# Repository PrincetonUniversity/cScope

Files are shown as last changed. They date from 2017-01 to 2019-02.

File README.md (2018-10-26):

# cScope 
A Head Mounted Widefield Macroscope 

This Github repository is meant to distribute the files accompanying the manuscript "Imaging cortical dynamics in GCaMP transgenic rats with a head-mounted widefield macroscope" by Benjamin Scott, Stephan Thiberge, Caiying Guo, Dougal Tervo, Carlos Brody, Alla Karpova, David Tank to appear in Neuron Journal (https://doi.org/10.1016/j.neuron.2018.09.050).

The repository contains the hardware information needed to build the cScope macroscopes, and the software needed to run experiments and post-process the data.

Use the "Clone or Download" button on this page, and choose "Download .Zip" to download all the files contained in this repository. Alternatively, you can download individual files by navigating through the repository folders.

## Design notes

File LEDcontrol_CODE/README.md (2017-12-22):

# LEDs control

The Arduino folder contains the two arduino codes, DELAY and GATE, loaded respectively on Arduino 1 and Arduino 2 (see manuscript supplemental figure). 
For each arduino, two versions of the code are written for different camera speeds (frame rate of 30Hz and 60Hz).

The Matlab folder contains the code run on the "LED control" computer.

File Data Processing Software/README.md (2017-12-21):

# Data Processing Software

Included in this directory are MATLAB scripts for processing the data files generated by cScope.  In order to run these scripts you will need to have a folder containing the .avi files and a timestamp.dat file that are produced by the miniscope camera acquisition system.  We assume that you will also have a data file produced by the Bcontrol software available here: http://brodywiki.princeton.edu/bcontrol/index.php/Main_Page

In order to run the motion correction stage in the preprocessing pipeline you will also need to download NoRMCorre:
https://github.com/simonsfoundation/NoRMCorre

Proceed in the following order:
1) cScope_preprocessing (~ 1 hour)
2) Hemodynamic_correction or Hemodynamic_correction_version2 (~ 12 hours)
3) Widefield_analysis (< 1 hour)

Included in parentheses are the approximate runtimes for processing a ~150,000 frame movie on a MacBookPro with a 3.1 GHz Intel Core i7 processor and 16 GB 1867 MHz DDR3 memory.

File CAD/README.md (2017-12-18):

# CAD files

The DWFX file is best viewed with the online viewer from Autodesk (viewer.autodesk.com). It allows the whole cScope assembly to be visualized in 3D and facilitates its construction.

The "3D printed parts" folder contains the .STL files for all printed parts used in cScope. These files can be uplaoded and used directly for 3d printing. We have used the company 3dsystems.com and the following process, materials and finish: Process: Stereolithography (SLA), Material: High-Res ABS-Like Black (either Accura SL 7820, or Renshape 7820 / VisiJet SL Black), Standard Finish. When asked for units during order process, enter "mm". 

The "machineshop" folder contains the drawings for the few parts that require machining.

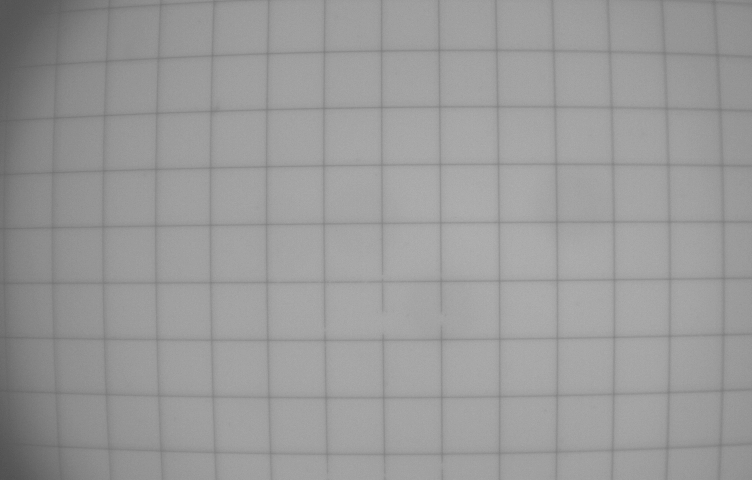
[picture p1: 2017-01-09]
DeformationCorrection/500umGrid.png

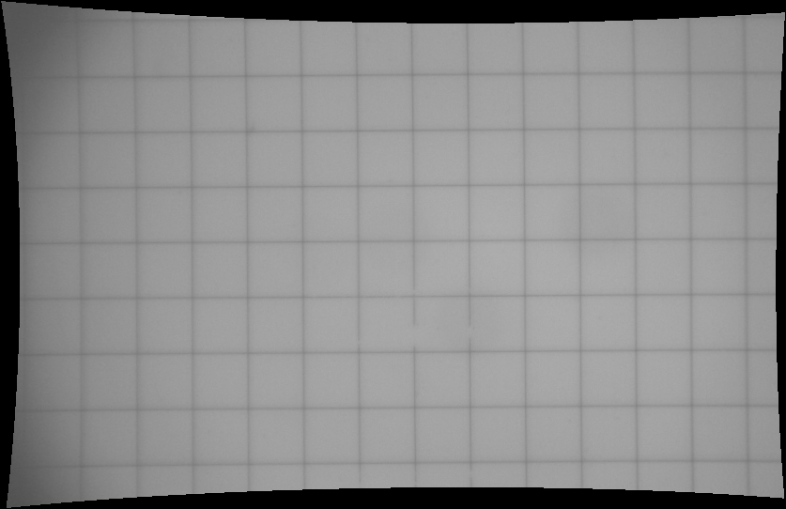
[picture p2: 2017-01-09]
DeformationCorrection/500umGrid_Unwarped.png

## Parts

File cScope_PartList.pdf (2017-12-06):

List of components for cScope. "Imaging cortical dynamics in GCaMP transgenic rats with a head mounted widefield macroscope” by Scott et al.

Label | Quantity | Unit | Part Number | Suggested Vendor | Description | Link | Approxi. Cost | Notes
| Lenses
CrW | 1 Ea | Custom part | TowerOptical
| | | | | N-BK7 Glass, 8mm*8mm, 3mm thick, flatness lambda/4 @ 633 nm, Surf
80/50 Scratch- Dig | http://www.toweroptical.com/ $13 Custom window, price/unit is for 25 units order
CrW | 1 Ea | Custom part | TowerOptical
| | | | | N-BK7 Glass, 8mm*4mm, 3mm thick, flatness lambda/4 @ 633 nm, Surf
80/50 Scratch- Dig | http://www.toweroptical.com/ $12 Custom window, price/unit is for 25 units order
L1 | 1 Ea | 45910 | Edmund Optics | N-SF11 Plano-Concave Lens, Ø6mm, f = -6.0 mm, VIS-NIR Coated | http://www.edmundoptics.com/optics/optical-lenses/plano-concave-pcv-spherical-singlet-lenses/vis-nir-coated-plano-concave-pcv-lenses/45910/ $39
L2 | 2 Ea | LA1560-A | Thorlabs | N-BK7 Plano-Convex Lens, Ø1/2", f = 25.0 mm, AR Coating: 350-700 nm | https://www.thorlabs.com/thorproduct.cfm?partnumber=LA1560-A $29
L3 | 1 Ea | LA1304-A | Thorlabs | N-BK7 Plano-Convex Lens, Ø1/2", f = 40.0 mm, AR Coating: 350-700 nm | https://www.thorlabs.com/thorproduct.cfm?partnumber=LA1304-A $28
L4 | 1 Ea | LB1450-A | Thorlabs | N-BK7 Bi-Convex Lens, Ø1/2", f = 20.0 mm, ARC: 350-700nm | https://www.thorlabs.com/thorproduct.cfm?partnumber=LB1450-A $32
L5 | 1 Ea | LC1054-A | Thorlabs
| | | | | N-BK7 Plano-Concave Lens, Ø1/2", f = -25.0 mm, AR Coating: 350-700
nm | https://www.thorlabs.com/thorproduct.cfm?partnumber=LC1054-A $27
L6 | 1 Ea | LA4765-A-SP | Thorlabs | UV Fused Silica Plano-Convex Lens, Ø1/2", f = 50.2 mm, AR Coating for 350nm-650nm | $127 This is a non-catalog item (the lens exist in catalog but not with this AR coating) The referenced item number is in the supplier's system and sales agent needs to be contacted to quote the item. Unit price indicated here is for an order of 5. Alternatively, the catlog item LA4765 can be used with the downside of several percent loss in signal.
L7 | 1 Ea | 47-269 | Edmund Optics | N-BK7 Half-Ball Lens, Ø3.0mm | http://www.edmundoptics.com/optics/optical-lenses/ball-condenser-lenses/n-bk7-half-ball-lenses/47269/ $31 Lens part of excitation path
L8 | 1 Ea | LB1494-A | Thorlabs | N-BK7 Bi-Convex Lens, Ø9.0 mm, f = 12.0 mm, ARC: 350-700nm | https://www.thorlabs.com/thorproduct.cfm?partnumber=LB1494-A $31 Lens part of excitation path

Filters and dichroic mirror
F1 | 1 Ea | ET470/40x | Chroma | Diced Excitation filter, 4.5 x 5 x 1mm | https://www.chroma.com/products/parts/et470-40x $25 - $50 These are custom diced filters. It is more cost effective to order 20 of each.
F2 | 1 Ea | ET525/50m | Chroma | Diced Emission filter, 14 x 15 x 1mm | https://www.chroma.com/products/parts/et525-50m $245 These are custom diced filters. It is more cost effective to order 5 of them.
F3 | 1 Ea | ET525/50m | Chroma | Diced Emission filter, 10 x 10 x 1mm | https://www.chroma.com/products/parts/et525-50m $200

This is the second emission filter set against the CMOS sensor. It is more cost effective to order several of them. Price is an estimate as we have not ordered this part ourselves, but diced this filter out of a 1" filter instead.

F4 | 1 Ea | FF496-SDi01-14x19.5-EB Semrock
| | | | 496 nm edge BrightLine® single-edge short-pass dichroic beamsplitter, 14
| | | | x 19.5 x 2mm, custom size, Edge Blacken | https://www.semrock.com/filterdetails.aspx?id=ff496-sdi01-25x36x2.0 $268

This is a custom diced dichroic. It is more cost effective to order several of them. Price given here is for an order of 2.

| 3D printed parts
Provide STL files with names changed to more helpful. Name_date will be the convention.
P1 | 1 Ea | Collar_16-dec22 | 3D Systems | SLA,High-Res ABS-Like (Black) (Renshape 7820 / VisiJet SL Black) | https://github.com/PrincetonUniversity/cScope $50 Note 1: Price is for an order of 3. Note 2: STL files can be used directly and sent for 3d printing. When asked for units during order process, enter "mm". https://www. 3dsystems.com/
P2 | 1 Ea | CollarCover | 3D Systems | SLA,High-Res ABS-Like (Black) (Renshape 7820 / VisiJet SL Black) | https://github.com/PrincetonUniversity/cScope $45 Notes 1 & 2.
P3 | 1 Ea | Objective | 3D Systems | SLA,High-Res ABS-Like (Black) (Renshape 7820 / VisiJet SL Black) | https://github.com/PrincetonUniversity/cScope $60 Notes 1 & 2.
P4 | 1 Ea | CoreBody | 3D Systems | SLA,High-Res ABS-Like (Black) (Renshape 7820 / VisiJet SL Black) | https://github.com/PrincetonUniversity/cScope $70 Notes 1 & 2.
P5 | 1 Ea | BodyFrontCover | 3D Systems | SLA,High-Res ABS-Like (Black) (Renshape 7820 / VisiJet SL Black) | https://github.com/PrincetonUniversity/cScope $55 Notes 1 & 2.
P6 | 1 Ea | BodySideCover | 3D Systems | SLA,High-Res ABS-Like (Black) (Renshape 7820 / VisiJet SL Black) | https://github.com/PrincetonUniversity/cScope $55 Notes 1 & 2.
P7 | 1 Ea | CameraSlider | 3D Systems | SLA,High-Res ABS-Like (Black) (Renshape 7820 / VisiJet SL Black) | https://github.com/PrincetonUniversity/cScope $53 Notes 1 & 2.
P8 | 0 Ea | Diffuser | 3D Systems | SLA,High-Res ABS-like,White | https://github.com/PrincetonUniversity/cScope $55 Notes 1 & 2. NOTE the material color is different from other pieces.
P9 | 1 Ea | HeadPlateCap | 3D Systems | SLA, material choice and color aren't critical | https://github.com/PrincetonUniversity/cScope $50 Notes 1 & 2. Use these window protective caps, if the collars are left attached at all times.
P10 | 1 Ea | CollarCap | 3D Systems | SLA, material choice and color aren't critical | https://github.com/PrincetonUniversity/cScope $50 Notes 1 & 2. Use these window protective caps, if the collars are removed when experiments are over.
P11 | 1 Ea | Rig_HeadPlate_Mounting1 3D Systems | SLA, material choice isn't critical | https://github.com/PrincetonUniversity/cScope $52
| | | | | RECOMMENDED. Jig used to assemble head plates and 3.5*8.0mm glass together before surgery. Note 2. Price is for quantity of 1.
P12 | 1 Ea | Rig_HeadPlate_Mounting2 3D Systems | SLA, material choice isn't critical | https://github.com/PrincetonUniversity/cScope $52
| | | | | RECOMMENDED. Jig used to assemble head plates and 8.0*8.0mm glass together before surgery. Note 2. Price is for quantity of 1.

Machined parts and stock material
Stock1 | 1 Ea | 89055K57 | McMaster-Carr | Titanium rod | https://www.mcmaster.com/#89055k57/=15qnw1y $32 Titanium stock to manufacture the head plates.
Stock2 | 1 Ea | SM05S10M | Thorlabs | Brass cylinder | https://www.thorlabs.com/thorproduct.cfm?partnumber=SM05S10M $8 Stock Brass cylinders to cut the two types of lens spacers needed in the optical assembly. One microscope requires 2 "thick" spacers and 1 "thin" spacer.
Stock3 | 1 Ea | 5HA14 | Grainger | Copper Shim Stock Roll, 110 Grade, 0.0030" Thickness | https://www.grainger.com/search?searchQuery=CUX-3 $111 Stock to cut Heat sinking of 480nm LED

List of components for cScope. "Imaging cortical dynamics in GCaMP transgenic rats with a head mounted widefield macroscope” by Scott et al.

Label | Quantity | Unit | Part Number | Suggested Vendor | Description | Link | Approxi. Cost | Notes
HP | 1 Ea | Headplate | local machine shop Titanium headplate for 3.5 by 8mm window | https://github.com/PrincetonUniversity/cScope --- Built from stock titanium rod above
HP | 1 Ea | Headplate | local machine shop Titanium headplate for 8 by 8mm window | https://github.com/PrincetonUniversity/cScope --- Built from stock titanium rod above
Sp1 | 1 Ea | LensesSpacer1 | local machine shop "Thin" Brass spacer | https://github.com/PrincetonUniversity/cScope --- Built from stock brass cylinders above
Sp2 | 2 Ea | LensesSpacer2 | local machine shop "Thick" Brass spacer | https://github.com/PrincetonUniversity/cScope --- Built from stock brass cylinders above
Cop | 1 Ea | CopperHeatSink | local machine shop "CopperShim" | https://github.com/PrincetonUniversity/cScope --- Built from stock copper shim above

Grids, and Resolution targets

Target1 | 1 Ea | R1L1S3P | Thorlabs | Star target | https://www.thorlabs.com/thorproduct.cfm?partnumber=R1L1S3P $220
| | | | | | | | Used to evaluate the Contrast Transfer Function. And RECOMMENDED to establish proper focus.
Target2 | 1 Ea | R1DS1P | Thorlabs | Positive 1951 USAF Test Target | https://www.thorlabs.com/thorproduct.cfm?partnumber=R1DS1P $125 OPTIONAL: Alternate and simple tool to evaluate system resolution
Target3 | 1 Ea | R1L3S3P | Thorlabs | Grid Distortion Target | https://www.thorlabs.com/thorproduct.cfm?partnumber=R1L3S3P $225 NECESSARY if using Matlab image deformation code provided

Microscope Core Body Assembly Jig
1 Ea | C1520 | Thorlabs | Adaptor plate | https://www.thorlabs.com/thorproduct.cfm?partnumber=C1520 $30 Useful Jig to place lenses within the core body of the objective
1 Ea | TR2 | Thorlabs | Ø1/2" Optical Post, L = 2" | https://www.thorlabs.com/thorproduct.cfm?partnumber=TR2 $5 Useful Jig to place lenses within the core body of the objective

LEDs powering

2 Ea | A000062 | Newark element14 Arduino Due | http://www.newark.com/arduino-org/a000062/dev-board-8e-arm-cortex-m3-arduino/dp/47W2961 $47
| | | | | | | | One arduino is used to delayDAQ card firing signal. The second is used to turn ON/OFF individual LED circuits (fluorescence source, intrinsic imaging source).
2 Ea | -- | Amazon, Ebay,... | USB male to USB microB | https://www.amazon.com/AmazonBasics-Male-Micro-Cable-Black/dp/B071S5NPG9/ref=sr_1_6?s=electronics&ie=UTF8&qid=1511272298&sr=1-6&keywords=USB+male+to+USB+microB $10 To connect Arduino to computer.
2 Ea | IRL540PBF-ND | Digikey | MOSFET N-CH 100V 28A TO-220AB, pack of 10 | https://www.digikey.com/product-detail/en/vishay-siliconix/IRL540PBF/IRL540PBF-ND/812025 $18
| | | | | | | | We built an enclosure in which 2 MOSFET (one for each LED circuits) were located. Wires run from that box to individual LEDs, to power supplies, and to arduino.
2 Ea | Resistors 300 kohms
| 4 Ea | BC-32671 | Digikey | Jumper wires (pack of 10 pieces) | http://www.digikey.com/product-detail/en/bud-industries/BC-32671/377-2263-ND/5291565 $5

Male-female jumper wires can be used to connect arduino to MOSFET and also be cut, pluged directly to arduino on one side and soldered to Banana/BNC terminals on the other.
FWir | 2 Ea | 9510T2 | McMaster Carr | Flexible wire for connecting LEDs (50ft per roll) (one Black and one White) https://www.mcmaster.com/#9510T2 $32 40-45ft are needed per microscope (4*10-12ft). Usefull to have several colors.
CP1 | 1 Ea | PRT-08233 | SparkFun ElectronicsPolarized Connectors - Header (2-Pin)- qty 25 | https://www.sparkfun.com/products/8233 $4

Male connector that inserts into the 3d printed collar connector for Green illumination (intrinsic imaging).
CP2 | 2 Ea | PRT-08100 | SparkFun ElectronicsPolarized Connectors - Crimp Pins (pack of 20) | https://www.sparkfun.com/products/8100 $2
| 1 Ea | CA2824 | Thorlabs | SMA Coaxial Cable, SMA Male to BNC Male | https://www.thorlabs.com/thorproduct.cfm?partnumber=CA2824 $16 Connects DAQ sync output to Arduino box
2 Ea | GPS-1830D | Newark element14 GW INSTEK GPS-1830D Bench Power Supply | http://www.newark.com/gw-instek/gps-1830d/power-supply-bench-adj-1o-p-18v/dp/79T9563?ost=72-6535&selectedCategoryId=&isexcsku=false&categoryNameResp=All%2BCategories&searchView=table&rpsku=rel1%3A726535 $199 used with the blue and green LEDs circuits.
LED2 | 4 Ea | LXZ1-PM01-SM-01A | Luxeon Star LEDs | Saber Micro-Z1 - LUXEON™ Z 5mm Square Single LED Module
| | | | Green - 103 lm (LXZ1-PM01) on Mounting Base (SM-01A) | http://www.luxeonstar.com/saber-micro-z1-luxeon-z-led-module $7
HS | 2 Ea | 345-1054-ND | DigiKey | Wakefield-Vette HEATSINK 14-16PIN DIP BLK - #651-B | https://www.digikey.com/product-detail/en/wakefield-vette/651-B/345-1054-ND/340350 $3
Alum | 1 Roll | 681975B | Amazon | adhesive Nashua Aluminum Foil Tape | https://www.amazon.com/dp/B0047XXZ7Q/ref=asc_df_B0047XXZ7Q5265072/?tag=hyprod-20&creative=394997&creativeASIN=B0047XXZ7Q&linkCode=df0&hvadid=167151102379&hvpos=1o3&hvnetw=g&hvrand=1990442287454641914&hvpone=&hvptwo=&hvqmt=&hvdev=c&hvdvcmdl=&hvlocint=&hvlocphy=9003941&hvtargid=pla-306995204863 (https://www.amazon.com/dp/B0047XXZ7Q?creative=394997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) $12
CMOS and fluorescence excitation LED are borrowed from the MINISCOPE project (UCLA) | miniscope.org
Here, we reproduce partially the list of items detailed in the miniscope.org website and used in cScope. Consulting the miniscope.org site and instructional videos therein is highly recommended.
LED1 | 1 Ea | LXML-PB01-0030 | Digikey | Excitation LED, LED LUXEON REBEL BLUE SMD (pack of 10) | http://www.digikey.com/product-detail/en/LXML-PB01-0030/1416-1028-1-ND/3961133 $4 This LED gets soldered onto the Exication LED PCB. See miniscope.org
PCB1 | 1 Ea | Silver Circuits | 2 layer, 0.031" Excitation LED PCB ($250 for 100 PCBs) | http://miniscope.org/index.php?title=Part_Procurement#Excitation_LED_PCB $3 Information, fabrication, and assembly files can be found at miniscope.org
COAX | 10 ft | CW2040-3650SR | Cooner Wire | 50ohm coax silicone rubber jacketed cable | http://www.coonerwire.com/mini-coax/ $80
CON | 1 Ea | CONSMA013.062 | Digikey | Edge Mount SMA Connector for use with Coax to SMA PCB | http://www.digikey.com/product-detail/en/CONSMA013.062/CONSMA013.062-ND/1577228 $5

This connector along with the Coax to SMA PCB below is the easiest way to connectorize the coax cable
SMA-PCB | 1 Ea | Miniscope Cable2SMA | OSH Park | 2 layer, 0.062" Coax to SMA PCB | https://oshpark.com/shared_projects/xtQGQ32E $1 This board can be used in conjunction with CONSMA013.062 above.
1 Ea | Amazon, ebay,.. | SuperSpeed USB3.0 Standard-A to Micro-B | https://www.amazon.com/AmazonBasics-USB-3-0-Cable-Male/dp/B00NH13G5A/ref=pd_lpo_vtph_147_tr_t_2?_encoding=UTF8&psc=1&refRID=R2AZGF6ZKQ4WEAZ50Q6K $6

Cable for connecting DAQ Box to computer. Using short cable is reommended (we used 1').
The two items below were ordered through the group orders organized by miniscope.org
CMOS | 1 Ea | CMOS Imaging Sensor PCBSierraCircuit | CMOS sensor mounted on PCB. One for each microscope. | http://miniscope.org/ | $115

Ordered through the miniscope.org. Sierra Circiuts handles sourcing the electrical components, PCB fabrication, and PCB assembly

1 Ea | DAQ PCB | SierraCircuit | DAQ to which camera is connected. One needed for each running microscope. http://miniscope.org/ | $200

Ordered through the miniscope.org. Sierra Circiuts handles sourcing the electrical components, PCB fabrication, and PCB assembly

List of components for cScope. "Imaging cortical dynamics in GCaMP transgenic rats with a head mounted widefield macroscope” by Scott et al.

Label | Quantity | Unit | Part Number | Suggested Vendor | Description | Link | Approxi. Cost | Notes
Hardware
S1 | 4 screw 96817A036 | McMaster-Carr | M1.2x4mm, Thread-Forming Screws for Thin Plastic, pack of 25 | https://www.mcmaster.com/#96817a036/=15p3dm6 $10
S2 | 4 screw 96817A011 | McMaster-Carr | M1.0x4mm, Thread-Forming Screws for Thin Plastic, pack of 25 | https://www.mcmaster.com/#96817a011/=15p3df5 $10
S3 | 5-10 screw 96817A009 | McMaster-Carr | M1.0x3mm, Thread-Forming Screws for Thin Plastic, pack of 25 | https://www.mcmaster.com/#96817A009 $10
S4 | 2 screw 95868A130 | McMaster-Carr | 2-56 Nylon Socket Head Screws, pack of 100 | https://www.mcmaster.com/#95868a130/=15p3jdr $10 Used to tighten the microscope in place once sled into the collar.
S5 | 1 screw 92311A313 | McMaster-Carr | 2-56 , 18-8 Stainless Steel Cup-Point Set Screw, pack of 100 | https://www.mcmaster.com/#92311a313/=15p3kfg $11 Used to tigthen collar in place once screwed on the head plate
S6 | 2 screw 91251A052 | McMaster-Carr | 0-80, 18-8 Stainless Steel Cup-Point Set Screw, pack of 50 | https://www.mcmaster.com/#91251a052/=15qoufv $3 Used to tighten the focussing arm in position
PTFE | 1 roll | 6305A42 | McMaster-Carr | Ultra-Slippery Tape (Made with Teflon® PTFE), General Purpose, 1/4" Width x 18 Yards Length https://www.mcmaster.com/#6305a42/=15p3r4q $16
VIT | 3 in | 96515K11 | McMaster Carr | Round-Profile Multipurpose O-Ring Cord Stock, Viton®, 1/32 Fractional Width, length 10 ft https://www.mcmaster.com/#96515k11/=15p40u4 $11 Rubber cord for filling in any gaps between the core body and filters/dichroic
BAF | 1 Ea | T205-1.0 | Thorlabs | Black Aluminum Foil Tape | https://www.thorlabs.com/thorproduct.cfm?partnumber=T205-1.0 $29 Used to create a baffle glued to the backside of the dichroic mirror
COP | 1 Ea | 9709K85 | McMaster Carr | Copper Shim Stock 6" x 50" Roll, 0.003" Thick | https://www.mcmaster.com/#9709k85/=1aa4j2m $28 Used to improve heat transfer from the blue LED
HS | 1 Ea | HS-ASST-9 | Newark element14 assorted heat shrink tubing including small diameter 1/16" | http://www.newark.com/nte-electronics/hs-asst-9/heat-shrink-tubing-assortment/dp/32M2893?CMP=KNC-GUSA-GEN-KWL-REM-PUR_NO-CART&mckv=|pcrid|102663440181|&gclid=CjwKEAiAkajDBRCRq8Czmdj-yFgSJADikZggS0F7SuIW9Eux23ywB--qNJFCxV9O_YWMRwkMO07NkxoCQtHw_wcB $17
| | | | | | | | Insulate soldered connections such as 2-pin connector. Many other similar products will do.

Tools and lab supplies

Tool1 | 1 Ea | VP10C | Thorlabs | Vacuum Pick-Up Tool | https://www.thorlabs.com/thorproduct.cfm?partnumber=VP10C $66

Can be used to manipulate lenses. Note that subsequent lens surface cleaning is often necessary.
Tool2 | 1 Ea | TZ1 | Thorlabs | Optic Tweezers w/ Carbon-Fiber Tips | https://www.thorlabs.com/thorproduct.cfm?partnumber=TZ1 $46 To handle lenses
Tool3 | 1 Ea | NOA61 | Thorlabs | Optical adhesive | https://www.thorlabs.com/thorproduct.cfm?partnumber=NOA61 $33 Used to secure all lenses in the 3d printed parts
Tool4 | 1 Ea | CS2010 | Thorlabs | UV curing system | https://www.thorlabs.com/thorproduct.cfm?partnumber=CS2010 $2,020 To polymerize Norland Optical Adhesive
Tool5 | 1 Ea | WES51 | Digikey | SOLDER STATION ANALOG 50W | http://www.digikey.com/product-detail/en/WES51/WES51-120V-ND/526397 $130 Soldering iron with temperature control is highly recommended
Tool6 | 1 Ea | 301 | Digikey | VISE 2.25" NYLON JAWS | http://www.digikey.com/product-detail/en/301/301PV-ND/1500 $55

Useful vice for holding PCBs during soldering. Useful for holding microscope 3d printed parts during assembly process.
Tool7 | 1 Ea | 386844 | Digikey | 63/37 400 2% .015DIA/28SWG Solder | http://www.digikey.com/product-search/en?keywords=82-117-ND $15 Suggested solder
Tool8 | 1 Ea | CW8400 | Digikey | FLUX DISPENSING PEN LEAD-FREE | http://www.digikey.com/product-search/en?keywords=CW8400 $15 Flux pen to aid in soldering
Tool9 | 1 Ea | ST-450 | Digikey | WIRE STRIPPER 26-36AWG | http://www.digikey.com/product-detail/en/ST-450/K545-ND/1990301 $41 Small gauge wire stripper
Tool10 | 1 Ea | PA70058 | Digikey | WIRE STRIPPERS 22-10, 30-20AWG | http://www.digikey.com/product-detail/en/PA70058/PA70058-ND/1991924 $21 Wire stripper
Tool11 | 1 Ea | 2522A771 | McMaster Carr | Through-hole Tap, 0-80 Thread | https://www.mcmaster.com/#2522a771/=15p41qh $12 Tap for set screw holes
Tool12 | 1 Ea | 26955A21 | McMaster Carr | Through-hole Tap, 2-56 Thread | https://www.mcmaster.com/#26955a21/=15p42ek $10 Tap for set screw holes
Tool13 | 1 Ea | 4261A58 | McMaster Carr | Precision Needle File, Rectangular, Finish No. 2, 6-1/4" Long | https://www.mcmaster.com/#4261a58/=15p431g $15 Precision file for cleaning up Delrin parts
Tool14 | 1 Ea | 52995A24 | McMaster Carr | Miniature Precision Torx Driver, Size T2 | https://www.mcmaster.com/#52995a24/=15p3wno $7 Driver for self threading M1 screws.
Tool15 | 1 Ea | 52995A26 | McMaster Carr | Miniature Precision Torx Driver, Size T3 | https://www.mcmaster.com/#52995a26/=15p3wep $6 Driver for self threading M1.2 screws.
Tool16 | 1 Ea | ONE 199L-QP | TCPGlobal | Black 1-Shot Lettering Enamels | http://www.tcpglobal.com/ONE-199L-QP.html?sc=119&category=3650941#.WGbJvdUrK70 $10 Not required but suggested for blackening filters edge
Tool17 | 1 Pk | 4001-BG10 | Grainger | Hardman Double Bubble Red Extra Fast Setting Epoxy (3-5 minute) (pack of 10) https://www.grainger.com/product/HARDMAN-Epoxy-3KYZ1 $28 suggested 5min epoxy
Tool18 | 1 Ea | -- | ebay,amazon... | Through-hole Tap, M14x0.75 Thread | --- | $25

multiple sources available on Ebay, Amazon,... This tap is used to correct for the inperfections of the 3d printed collar thread.
Tool19 | 1 Pk | Grainger | Fine sand paper | Used to clean up and open collar inner diameter, and objective
Tool20 | 1 Ea | C1520 | Thorlabs | Adaptor plate | https://www.thorlabs.com/thorproduct.cfm?partnumber=C1520 $30 Useful Jig to place lenses within the core body of the objective
Tool21 | 1 Ea | TR2 | Thorlabs | Ø1/2" Optical Post, L = 2" | https://www.thorlabs.com/thorproduct.cfm?partnumber=TR2 $5 Useful Jig to place lenses within the core body of the objective
Tool22 | 1 box | MC-5 | Thorlabs | Lens Tissues | https://www.thorlabs.com/thorproduct.cfm?partnumber=MC-5 $10
Tool23 | 1 Pk | CTA10 | Thorlabs | Cotton-Tipped Applicators (pk of 100) | https://www.thorlabs.com/thorproduct.cfm?partnumber=CTA10 $4
Tool24 | 1 Ea | CA3 | Thorlabs | Air duster | https://www.thorlabs.com/thorproduct.cfm?partnumber=CA3 $12
Tool25 | 1 Bottle | -- | --- | Optical grade Methanol | --- | ---
Tool26 | 1 Ea | -- | Mcmaster Carr | Adjustable-Arm Illuminated Magnifier | https://www.mcmaster.com/#lighted-magnifiers/=15r7w7s $150 OPTIONAL: Parts are small. This helps a lot.
Tool27 | 1 Ea | Multimeter | testing LED circuit
Tool28 | 1 Ea | AATA-5G | Newark element14 Artic Silver | http://www.newark.com/arctic-silver/aata-5g/adhesive-thermal-syringe-5g/dp/71T6886?CMP=KNC-GUSA-GEN-KWL-REM-ABANDONED&mckv=|pcrid|190494399039|&gclid=CjwKCAiAxarQBRAmEiwA6YcGKPklFlzmlwRQZjhqT6aEuuk3Q0ym1OndNI7Hx4DxxvXxszfzAnBJEBoCShcQAvD_BwE $15 Thermal adhesive used in the Blue LED heat sinking procedure

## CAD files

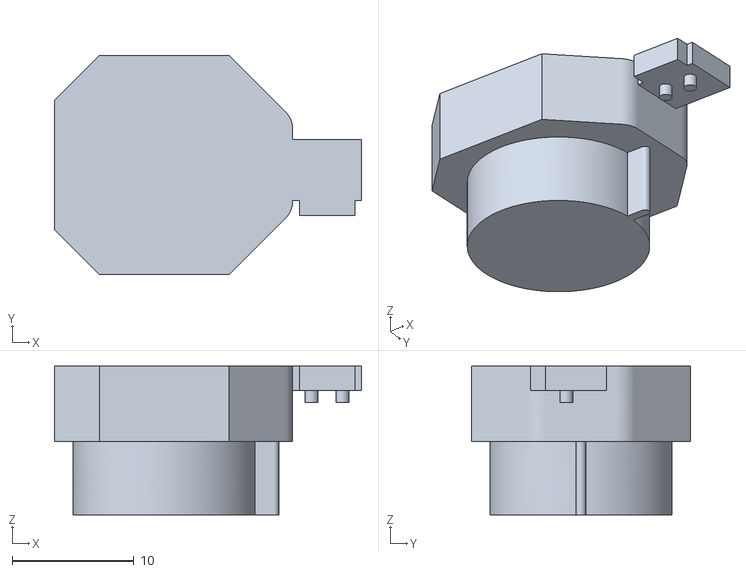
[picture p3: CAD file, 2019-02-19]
CAD/3DprintFiles/P10_CollarCap.stl
25.2 x 18.0 x 12.2

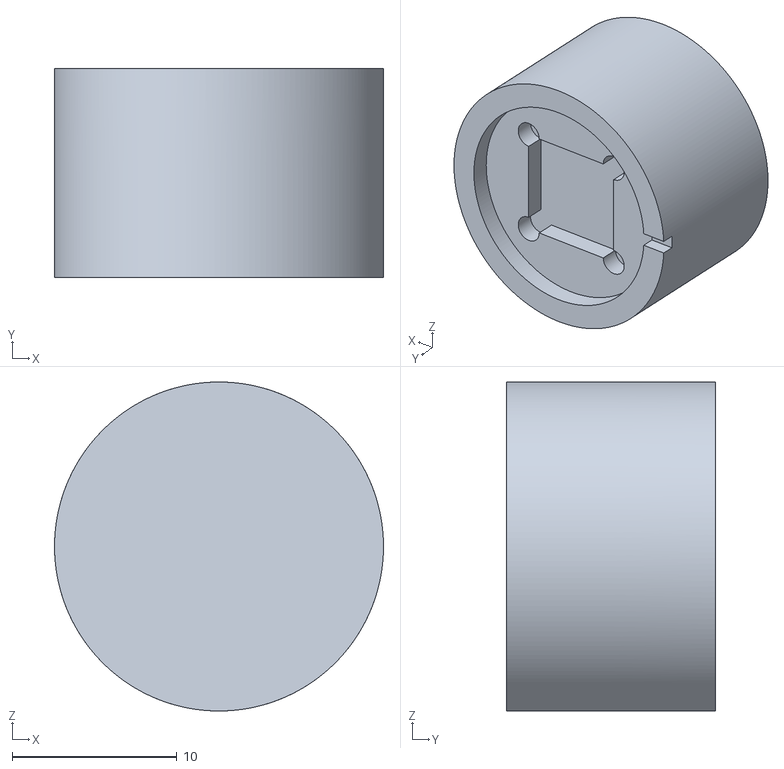
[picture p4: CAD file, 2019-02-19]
CAD/3DprintFiles/Rig_HeadPlate_Mounting2.stl
20.0 x 12.7 x 20.0

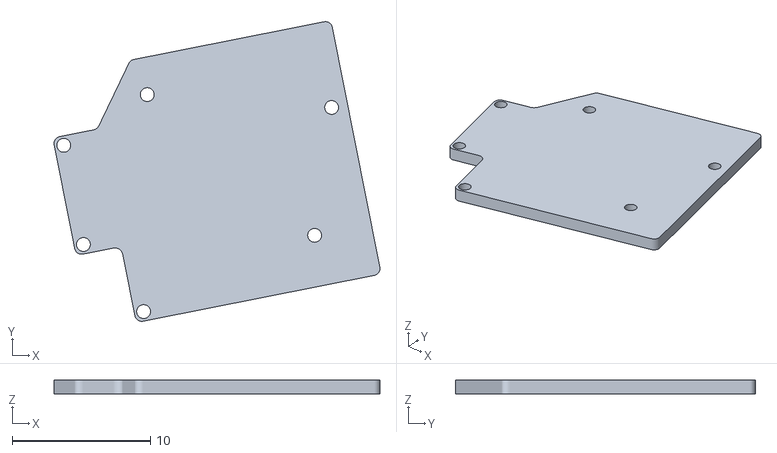
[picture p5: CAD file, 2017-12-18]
CAD/3DprintFiles/P6_BodySideCover_12122017.stl
23.5 x 21.6 x 1.00

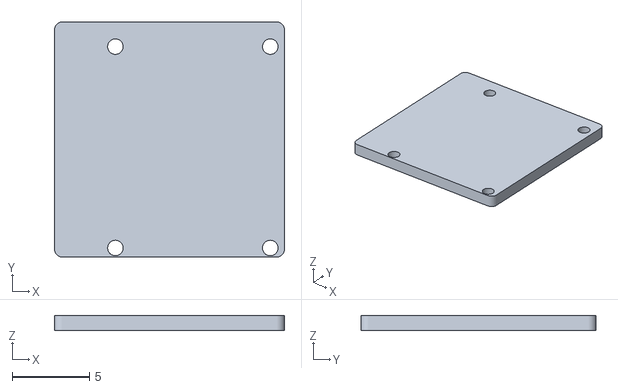
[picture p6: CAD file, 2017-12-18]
CAD/3DprintFiles/P5_BodyFrontCover_12122017.stl
14.8 x 15.2 x 1.00

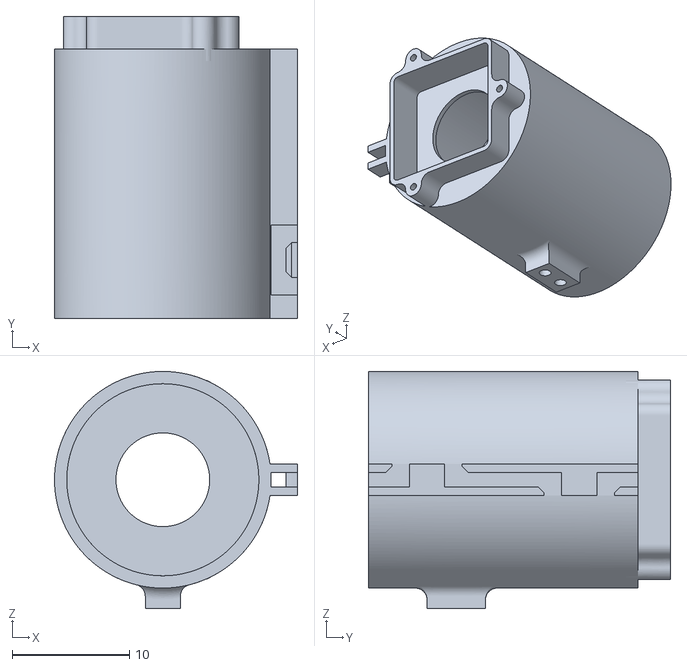
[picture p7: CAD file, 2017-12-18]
CAD/3DprintFiles/P7_CameraSlider_12122017.stl
20.8 x 25.8 x 20.2

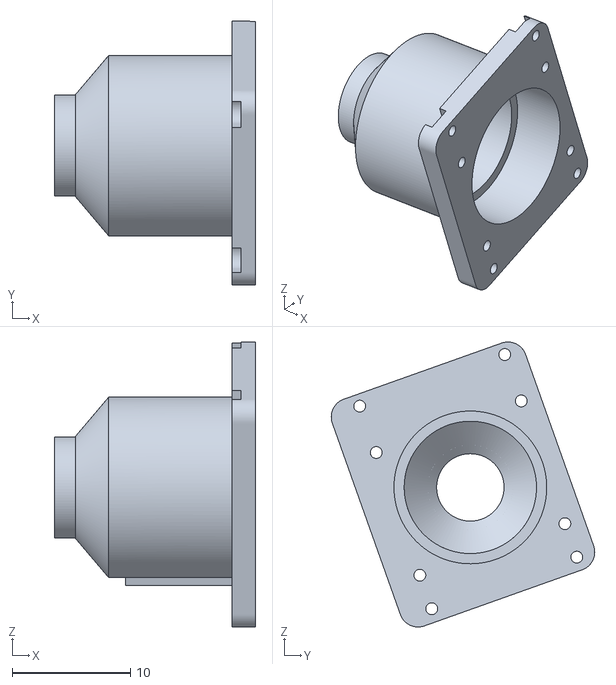
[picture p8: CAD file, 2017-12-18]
CAD/3DprintFiles/P3_Objective_12122017.stl
17.0 x 22.3 x 24.1

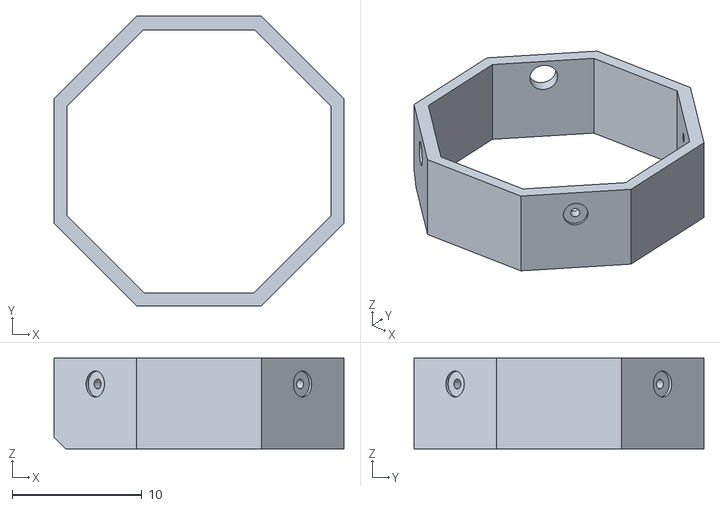
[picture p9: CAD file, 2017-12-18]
CAD/3DprintFiles/P2_CollarCover_12122017.stl
22.3 x 22.3 x 7.00

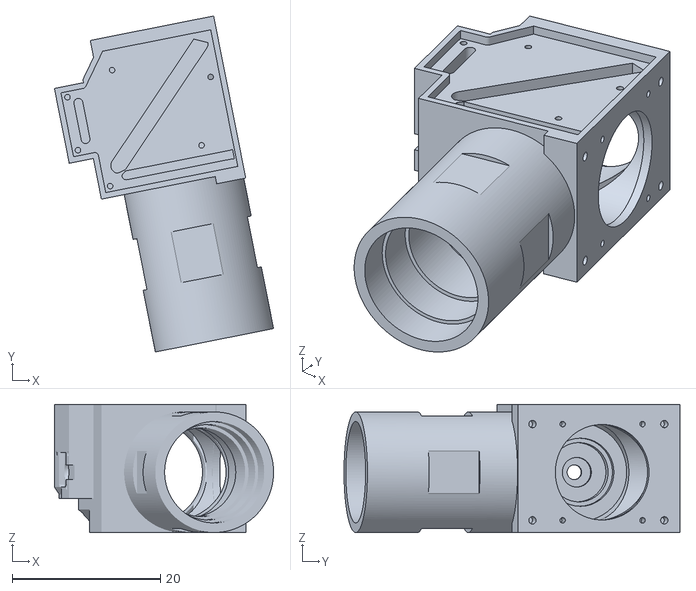
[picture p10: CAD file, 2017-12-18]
CAD/3DprintFiles/P4_CoreBody_12122017.stl
29.6 x 45.4 x 17.3

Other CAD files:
CAD/3DprintFiles/Rig_HeadPlate_Mounting1.stl

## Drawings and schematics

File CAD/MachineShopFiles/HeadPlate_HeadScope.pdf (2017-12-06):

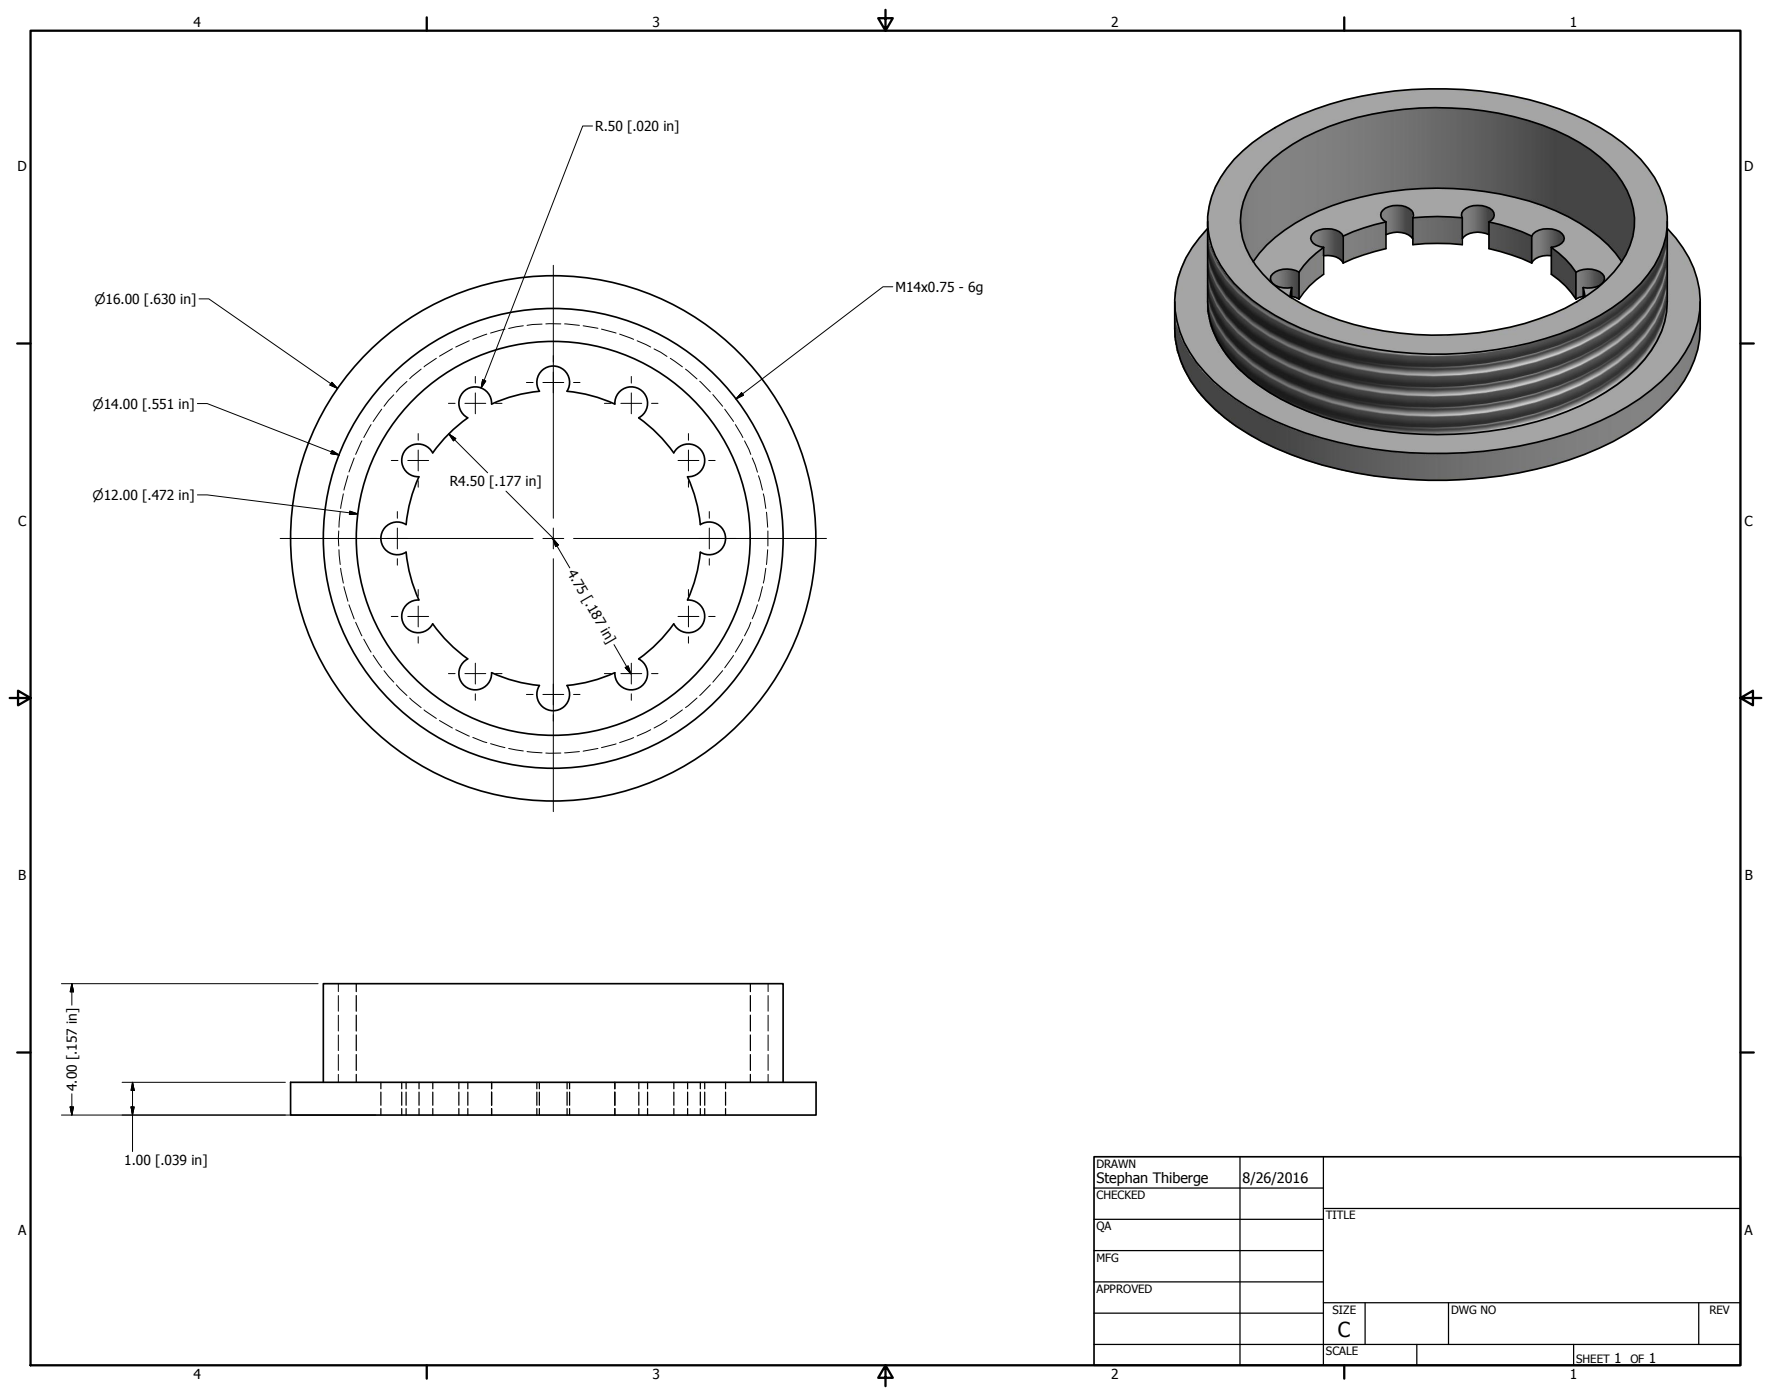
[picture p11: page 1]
SHEET 1 OF 1; DRAWN; CHECKED; MFG; APPROVED; Stephan Thiberge; DWG NO; TITLE; SIZE C; SCALE; REV

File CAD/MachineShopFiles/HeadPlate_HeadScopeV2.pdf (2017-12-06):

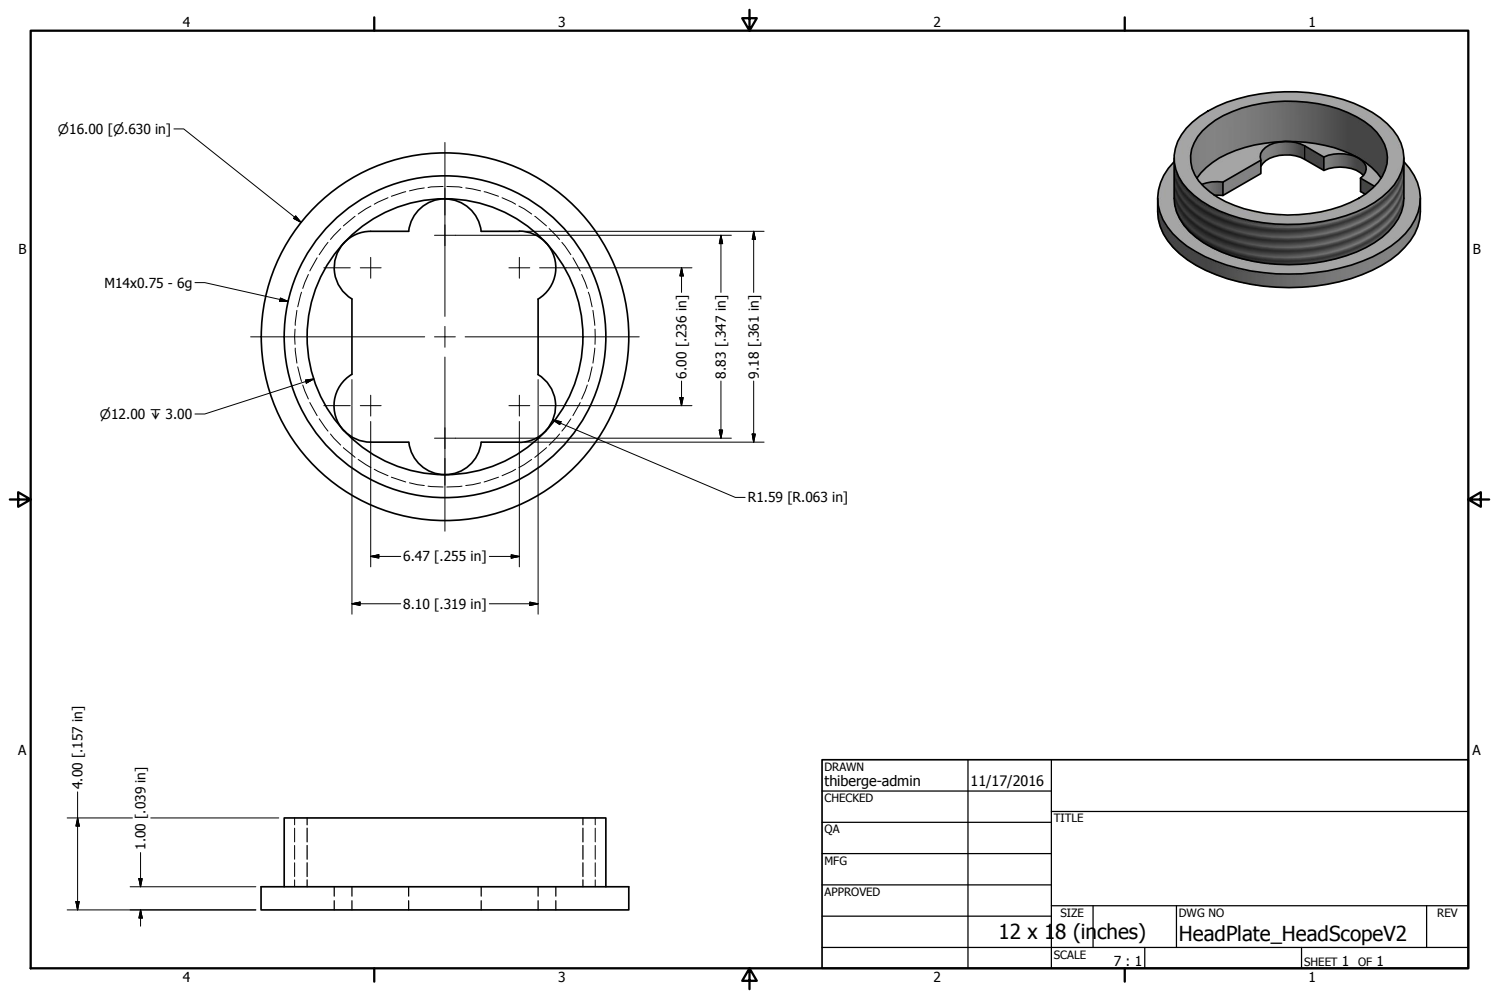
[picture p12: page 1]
SHEET 1 OF 1; DRAWN; CHECKED; MFG; APPROVED; thiberge-admin; DWG NO HeadPlate_HeadScopeV2; TITLE; SIZE 12 x 18 (inches); SCALE; REV

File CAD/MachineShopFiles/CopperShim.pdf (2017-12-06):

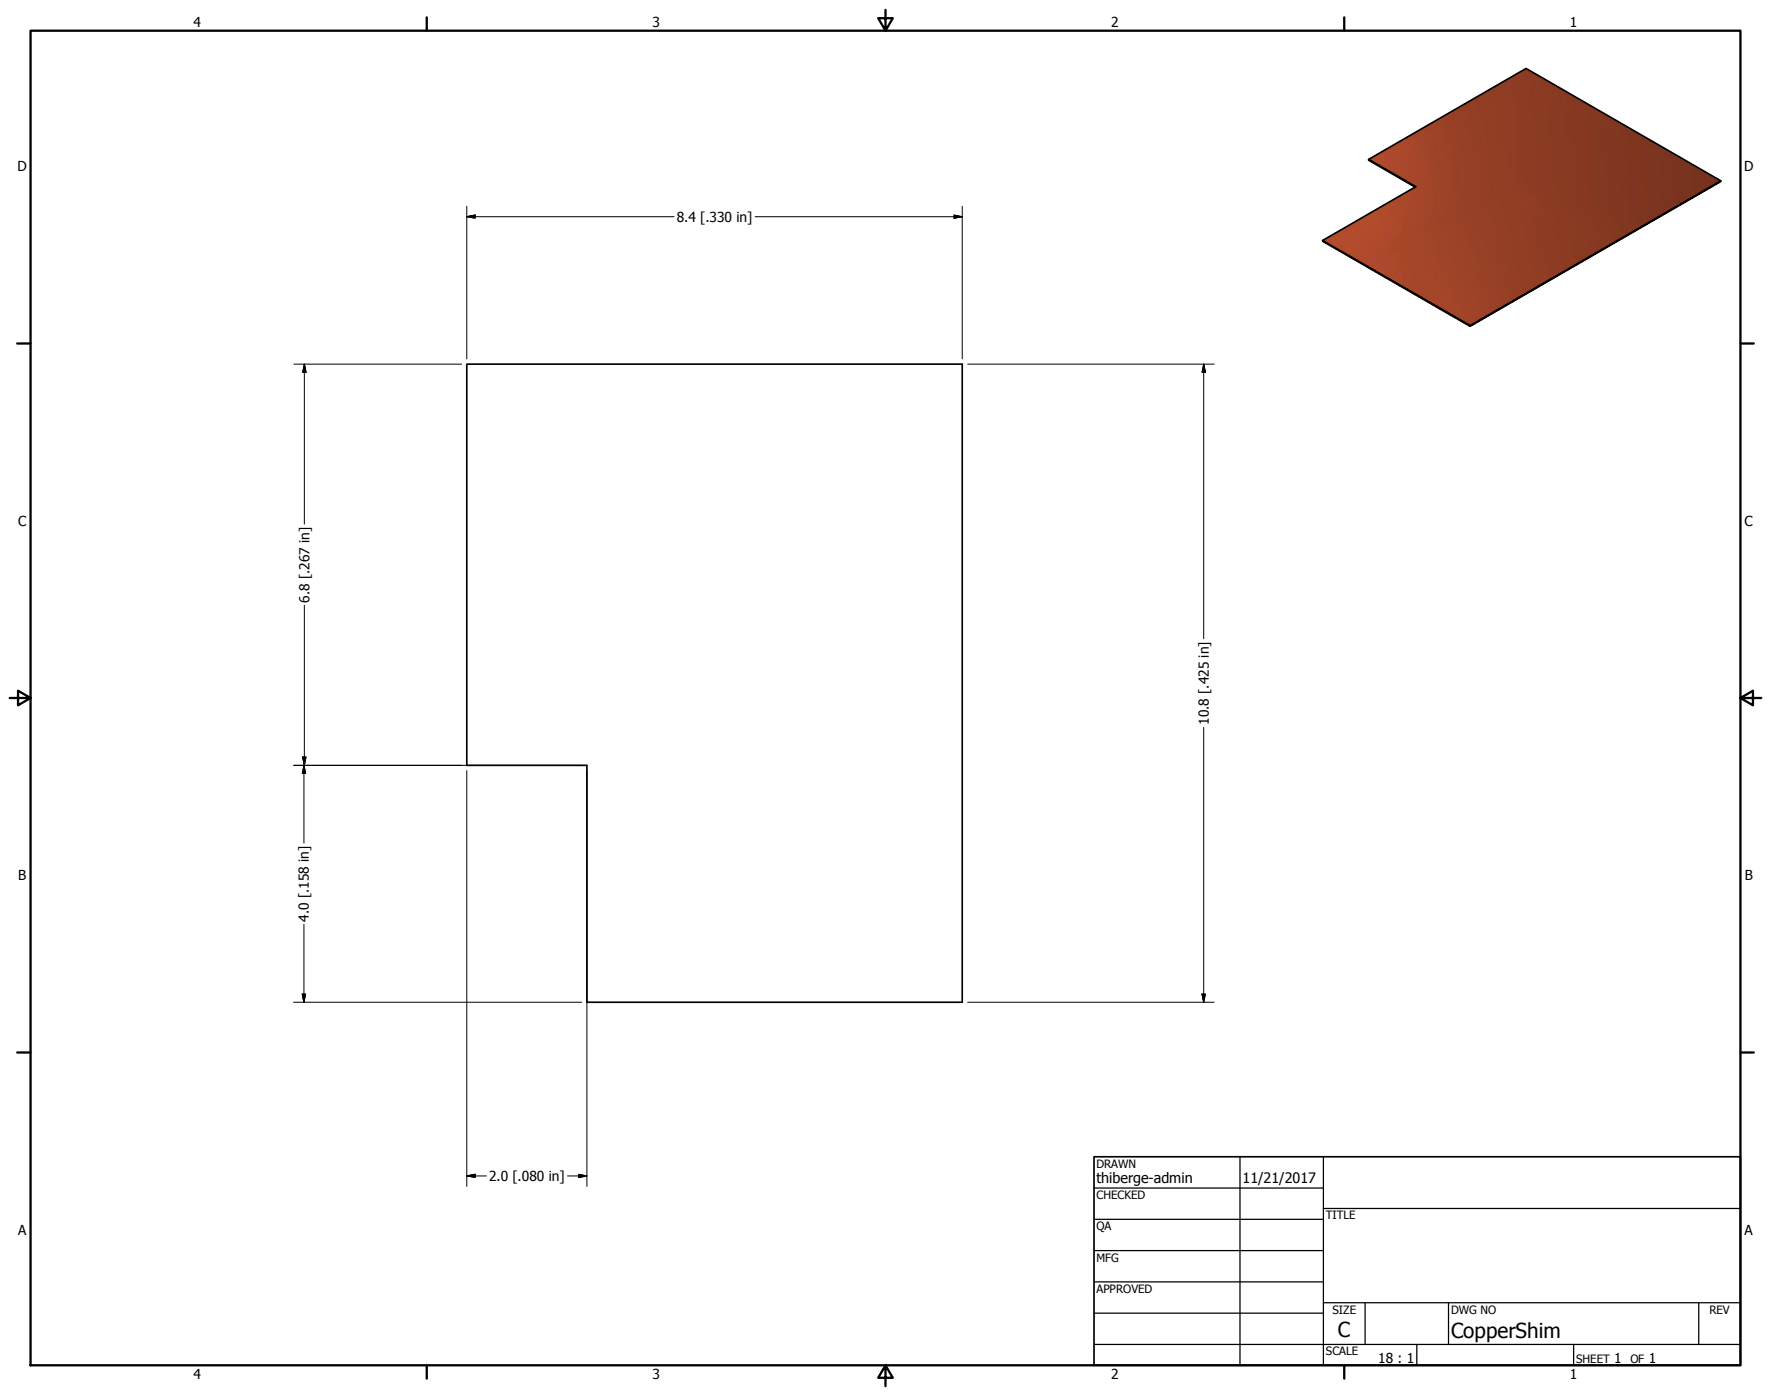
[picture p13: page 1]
SHEET 1 OF 1; DRAWN; CHECKED; MFG; APPROVED; thiberge-admin; DWG NO CopperShim; TITLE; SIZE C; SCALE; REV

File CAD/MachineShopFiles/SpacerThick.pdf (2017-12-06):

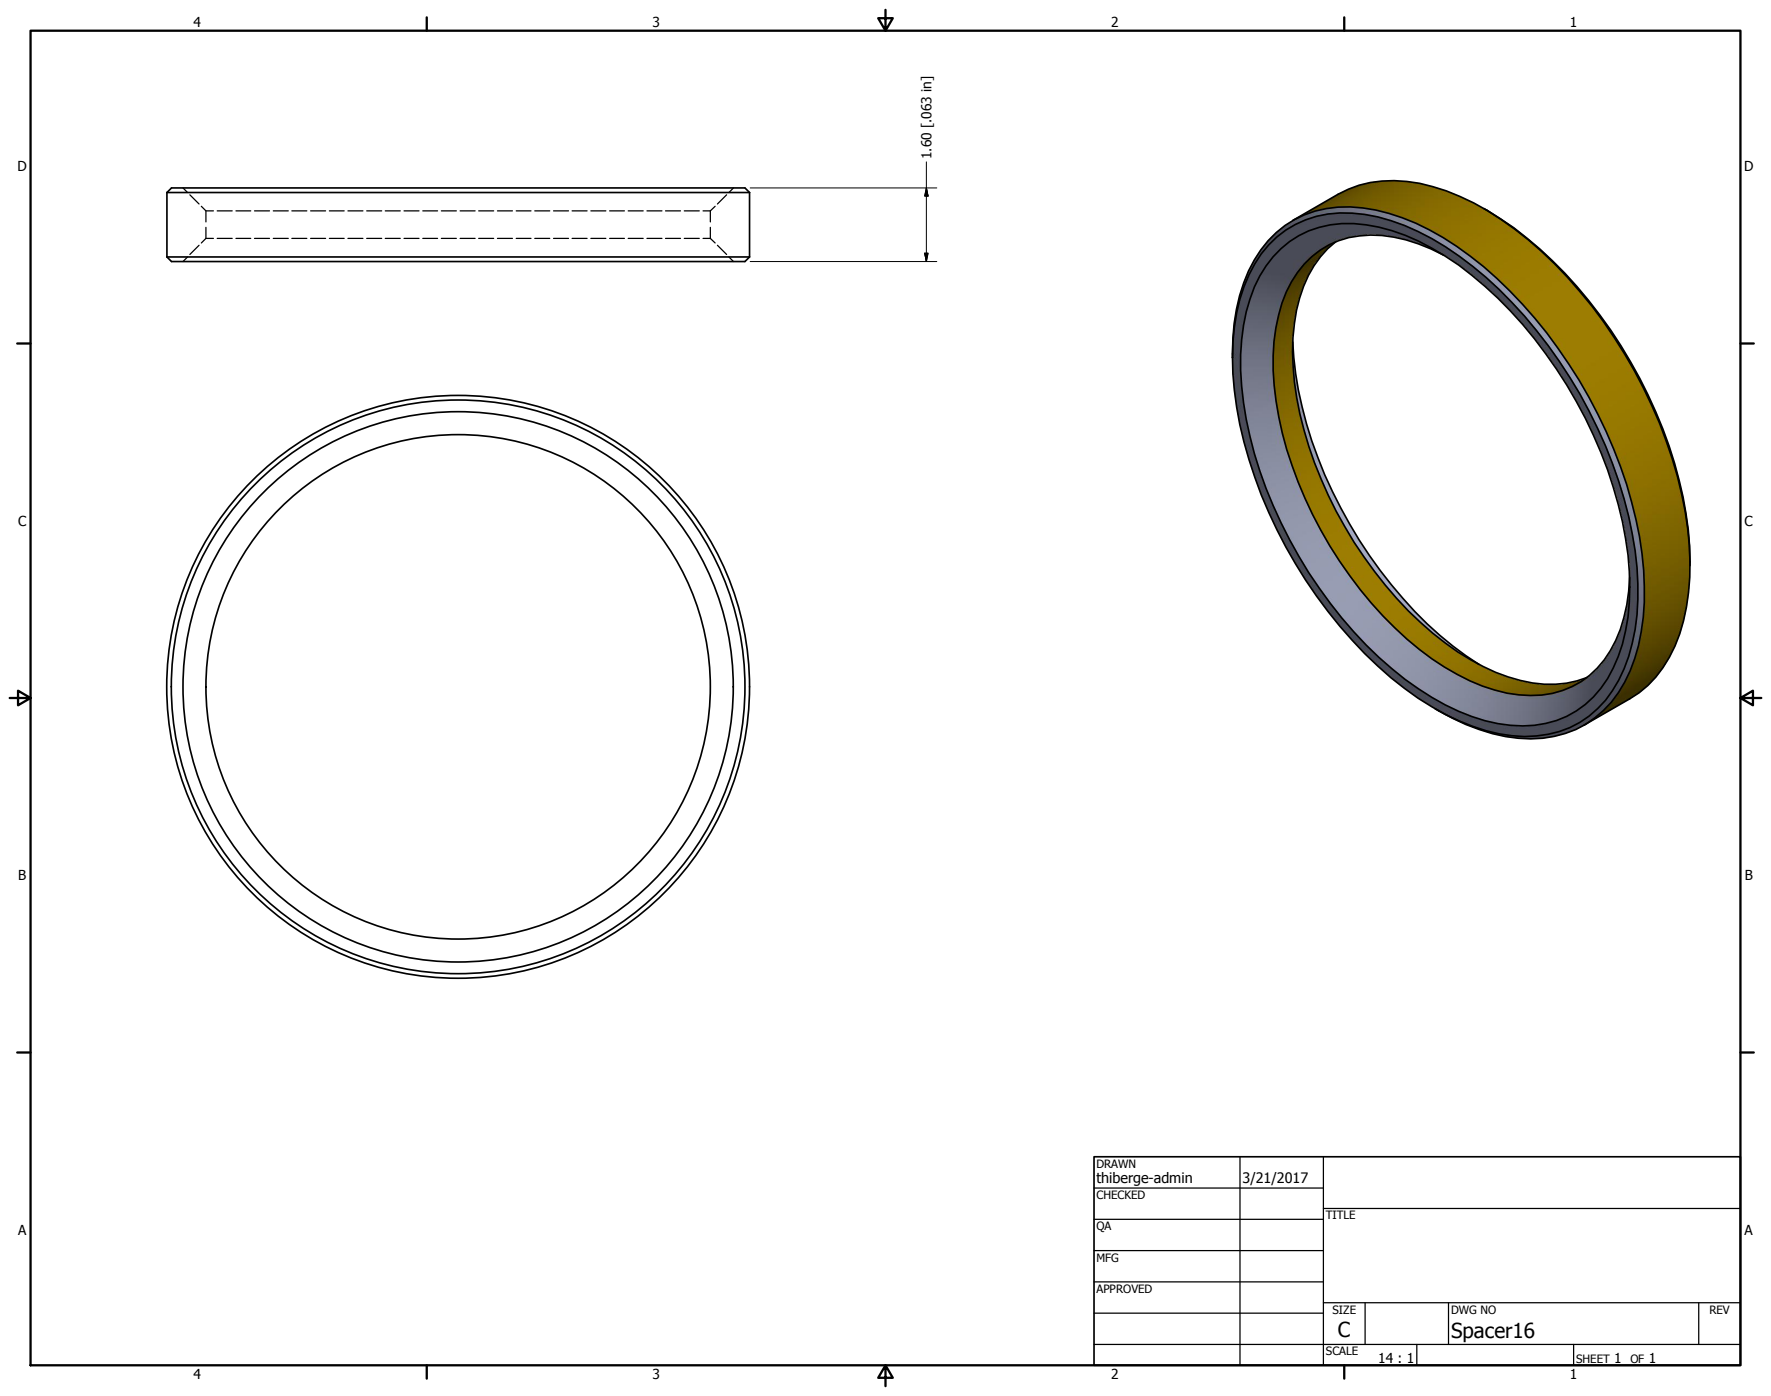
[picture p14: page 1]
SHEET 1 OF 1; DRAWN; CHECKED; MFG; APPROVED; thiberge-admin; DWG NO Spacer16; TITLE; SIZE C; SCALE; REV

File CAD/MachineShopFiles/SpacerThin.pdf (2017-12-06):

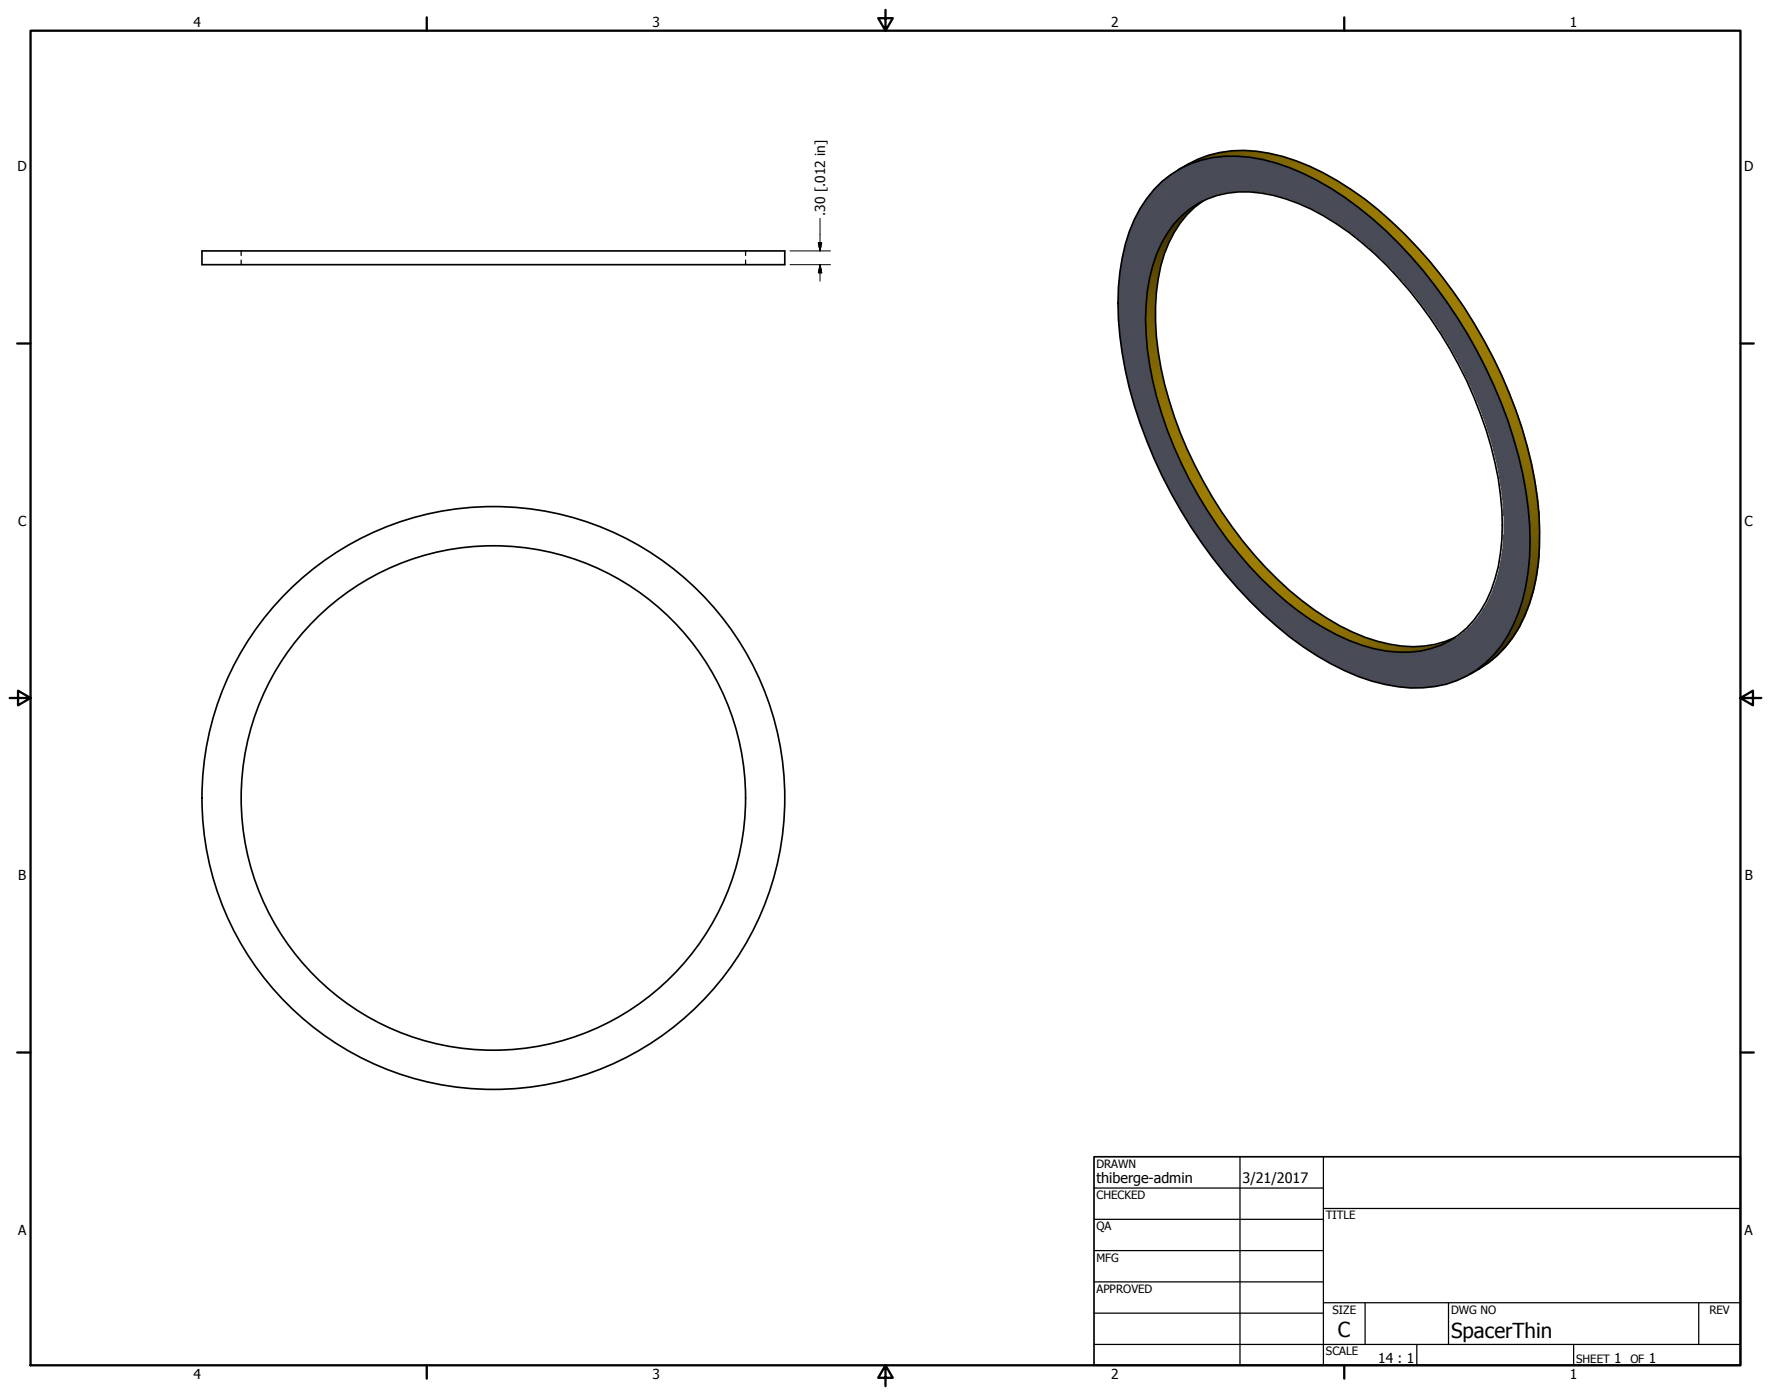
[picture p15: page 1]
SHEET 1 OF 1; DRAWN; CHECKED; MFG; APPROVED; thiberge-admin; DWG NO SpacerThin; TITLE; SIZE C; SCALE; REV

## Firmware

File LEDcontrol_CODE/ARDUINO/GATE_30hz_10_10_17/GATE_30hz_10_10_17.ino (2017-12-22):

/***************************************************************
 * This code allows one to toggle and strobe  TTL logic driven 
 * illumination sources using anArduino microcontroller 
 * (up to a maximum of 9) in any order.
 ****************************************************************/

/***************************************************************
 * Select the strobe TTL logic used by your illumination source. 
 * Here, the macro LED_ON corresponds to the TTL signal level used 
 * to turn the illumination source on while LED_OFF corresponds
 * to the TTL signal level used to turn the illumination source off.
 * These values are used to set the logic state of Arduino digital
 * output pins
 ****************************************************************/
#define LED_ON HIGH
#define LED_OFF LOW

//Define how many sources will be strobed
#define LENGTH_LED_ARRAY 2

//Global variables
volatile int incoming_value;
volatile int value;
int *LED_order = NULL;
volatile int LED_array[] = {DAC0,DAC1};//{52,51};//{8,10,12,6}; //these pins have LEDs attached to them.
//volatile int Exposure_Output_pin=4; //this pin outputs the exposure signal read from the camera.

volatile int Stim_Delay_pin=38;
//volatile int Stim_Delay_state=0;

volatile int ledToggleIndex = 0;
volatile int numberOfElements = 0;
volatile int nextLED=0;
volatile int start_delay=1;

//volatile int DelayedPulseOutput_pin=47; 
//volatile int Stim_DelayPulse_pin=39;
//volatile int Stim_DelayPulse_state=0;

volatile int state=0;


volatile int Bcontrol_pin=31;
volatile int Gatestate=LOW;


void setup()
{
  SerialUSB.begin(9600);
  for (int i=0; i<1; i++)
  {
    pinMode(LED_array[i],OUTPUT);
    //digitalWrite(LED_array[i],LED_OFF);
      analogWrite(LED_array[i],0);
  }
  pinMode(Stim_Delay_pin,INPUT);
//  pinMode(Exposure_Output_pin,OUTPUT);
//  digitalWrite(Exposure_Output_pin,LED_OFF); 
  
//  pinMode(Stim_DelayPulse_pin,INPUT);
//  pinMode(DelayedPulseOutput_pin,OUTPUT);
//  digitalWrite(DelayedPulseOutput_pin,LOW);

 //gating functionality
 pinMode(Bcontrol_pin,INPUT);        //input pin
 digitalWrite(digitalPinToInterrupt(Bcontrol_pin),LOW);
 
}

void loop()
{
  while (SerialUSB.available()>0)
  {
    incoming_value = SerialUSB.read();
    switch (incoming_value)
    {
    case 99: // c
      detachInterrupt(digitalPinToInterrupt(Stim_Delay_pin));
//      detachInterrupt(digitalPinToInterrupt(Stim_DelayPulse_pin));
      turn_off_all_LEDs();
      if (NULL != LED_order)
      {
        free(LED_order);
        LED_order = NULL;
      }
      SerialUSB.print("Interrupts disabled"); 
      break;

    case 116:  // t
      // Turn off all LEDs first
      //SerialUSB.println("Toggle all LEDs OFF");
      turn_off_all_LEDs();

      delay(10);
      //SerialUSB.println("Toggle next LED ON");
      ledToggleIndex = SerialUSB.read() - 49;
      //SerialUSB.println(LED_array[ledToggleIndex], DEC);
      //digitalWrite(LED_array[ledToggleIndex], LED_ON);
      analogWrite(LED_array[ledToggleIndex], 255);
      SerialUSB.print(ledToggleIndex+1,DEC);   
      break;

    case 120: // x
      SerialUSB.println("Toggle all LEDs OFF");
      turn_off_all_LEDs();
      break;

    case 115: // s
      delay(10);
      // read number of available bytes
      numberOfElements = SerialUSB.available();

      // allocate array using malloc and initalize all elements to 0
      LED_order = (int *) malloc(numberOfElements * sizeof(int));
      for (int counter = 0; counter < numberOfElements; counter++)   {
        LED_order[counter] = 0;
      }

      // Read in strobe order
      for (int counter = 0; counter < numberOfElements; counter++)   {
        LED_order[counter] = SerialUSB.read() - 49;
      }

      SerialUSB.println("LED_order is:");
      for (int counter = 0; counter < numberOfElements; counter++)   {
        SerialUSB.println(LED_order[counter], DEC);
      }

      SerialUSB.println("Pin order");
      for (int counter = 0; counter < numberOfElements; counter++)   {
        SerialUSB.println(LED_array[LED_order[counter]], DEC);
      }

      nextLED=0;
      //digitalWrite(Exposure_Output_pin,LED_OFF);
      digitalWrite(digitalPinToInterrupt(Stim_Delay_pin),LOW);
     // digitalWrite(digitalPinToInterrupt(Stim_DelayPulse_pin),LOW);
      start_delay=1;
      ////attachInterrupt(digitalPinToInterrupt(Stim_Delay_pin), strobe_on_LEDs, RISING);
      ////attachInterrupt(digitalPinToInterrupt(Stim_Delay_pin_off), strobe_off_LEDs, FALLING);

     // attachInterrupt(digitalPinToInterrupt(Stim_DelayPulse_pin), DelayFramePulse, CHANGE);
      attachInterrupt(digitalPinToInterrupt(Stim_Delay_pin), strobe_on_LEDs, CHANGE);
      
      
      //attachInterrupt(0, strobe_on_LEDs, RISING);
      //attachInterrupt(1, strobe_off_LEDs, FALLING);
      SerialUSB.print("Interrupts enabled");
      break;  

//    case 114: //r
//      //digitalWrite(Stim_Delay_pin, LOW);
//      SerialUSB.print("Stim Trigger Reset");  
//      break;
//
//    case 82: //R
//      //digitalWrite(Stim_Delay_pin, HIGH);
//      SerialUSB.print("Stim Trigger Reset");  
//      break;

    case 97: //a
      SerialUSB.print("State reset");
      nextLED=0;
      break;

    case 102: //f
      SerialUSB.flush();
      SerialUSB.println("Flush");
      break;

//    case 77: //M (legacy from Matt's code to check comm status)
//      SerialUSB.println("I'm ready to get the data");
//      break;
//
//    case 100: //d -- Stim Delay read
//      Stim_Delay_state=digitalRead(Stim_Delay_pin);
//      if (Stim_Delay_state==1)
//      {
//        SerialUSB.print("Ready");
//      }
//      else
//      {
//        SerialUSB.print("Wait");
//      }
//      break;
    }
  }
}


void strobe_on_LEDs()
{
  if (start_delay==1){
    interrupts();
    delayMicroseconds(0); //5000 originally
    start_delay=0;
  }
  //SerialUSB.println(LED_array[LED_order[nextLED]]);



  Gatestate=digitalRead(Bcontrol_pin);
  //if the gate is LOW, skip turning ONthe LEDs
  if (Gatestate) 
  {value=0;} 
  else
  {value=255;}


  
  //digitalWrite(LED_array[LED_order[nextLED]], LED_ON);
  analogWrite(LED_array[LED_order[nextLED]], value);
  //digitalWrite(Exposure_Output_pin,LED_ON);

  // delayMicroseconds(500);
  //delayMicroseconds(9000); // do not exceed value 16383// both 30Hz and 60Hz
  delayMicroseconds(16000); //use also this one for 30Hz
  delayMicroseconds(2000); //use also this one for 30Hz
  //strobe_off_LEDs;
  //digitalWrite(LED_array[LED_order[nextLED]], LED_OFF);
      analogWrite(LED_array[LED_order[nextLED]], 0);
  //digitalWrite(Exposure_Output_pin,LED_OFF);
   if (nextLED < (numberOfElements - 2)) // hack: going to end-1 as matlab is sending an empty element
  {
    nextLED++;
  }
  else if (nextLED == (numberOfElements - 2))
  {
    nextLED = 0;
  }
}

//void DelayFramePulse()
//{
//  state=digitalRead(Stim_DelayPulse_pin);
//  delayMicroseconds(10000);
//  delayMicroseconds(7000);
//  digitalWrite(DelayedPulseOutput_pin,state);
//}

void strobe_off_LEDs()
{
  //digitalWrite(LED_array[LED_order[nextLED]], LED_OFF);
       analogWrite(LED_array[LED_order[nextLED]], 0);
  //digitalWrite(Exposure_Output_pin,LED_OFF);
  if (nextLED < (numberOfElements - 2)) // hack: going to end-1 as matlab is sending an empty element
  {
    nextLED++;
  }
  else if (nextLED == (numberOfElements - 2))
  {
    nextLED = 0;
  }
}

void turn_off_all_LEDs()
{
  for (int i=0; i < LENGTH_LED_ARRAY; i++)
  {
    //digitalWrite(LED_array[i], LED_OFF);
    analogWrite(LED_array[i], 0);    
  }
  //digitalWrite(Exposure_Output_pin,LED_OFF);
}

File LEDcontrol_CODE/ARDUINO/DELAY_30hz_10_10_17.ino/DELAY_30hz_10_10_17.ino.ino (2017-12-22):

/***************************************************************
 * This code reproducesthe an input Digital input on a digital output pin
 * after a fixeddelay.
 ****************************************************************/

//Global variables

volatile int DelayedPulseOutput_pin=47; 
volatile int Stim_DelayPulse_pin=39;

volatile int state=LOW;

void setup()
{
  
  pinMode(Stim_DelayPulse_pin,INPUT);        //input pin
  pinMode(DelayedPulseOutput_pin,OUTPUT);    //outputpin
  digitalWrite(DelayedPulseOutput_pin,LOW);
  
  digitalWrite(digitalPinToInterrupt(Stim_DelayPulse_pin),LOW);
  attachInterrupt(digitalPinToInterrupt(Stim_DelayPulse_pin), DelayFramePulse, CHANGE);

}

void loop()
{
 digitalWrite(DelayedPulseOutput_pin, state);
}


void DelayFramePulse()
{
  state=digitalRead(Stim_DelayPulse_pin);
  //delayMicroseconds(9000);//for 60Hz exposures
  delayMicroseconds(10000); //1- for 30Hz exposures
  delayMicroseconds(8000);  //2- for 30Hz exposures
}
